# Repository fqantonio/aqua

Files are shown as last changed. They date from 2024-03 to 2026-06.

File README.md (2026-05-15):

# GENERAL VIEW

> Portugal is 97% water [^1]

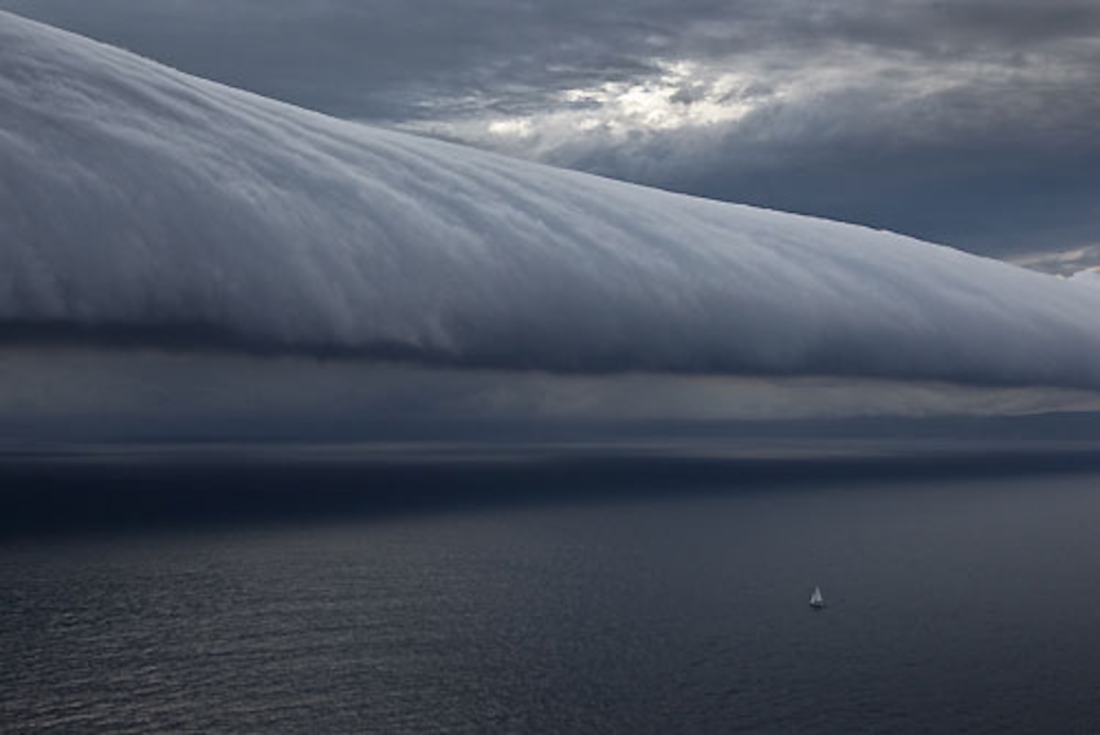
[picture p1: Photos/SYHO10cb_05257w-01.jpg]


*The southerly buster storm front rolling up the New South Wales South Coast, ahead of the first night at sea, after the start of the Rolex Sydney Hobart Yacht Race 2010, Australia. Photo © Carlo Borlenghi / Rolex. www.carloborlenghi.com.* 

## ABOUT AQUA

AQUA is a small autonomous vessel designed for biowater research and aquatic engineering education. This project's core strategy is to consider environmental sustainability from start to finish. All stages, from fabrication to the end of life, should be environmentally friendly.

The team's values are rooted in the **4R's (Reduce, Reuse, Recycle, Recover)** and **circular economy principles**, aiming to meet these standards by at least **70%**. The project also seeks to raise awareness about water and ocean systems, which is especially important since **Portugal's territory is 97% water**.

## MISSION

The goal is to construct an DIY affordable and easily maintainable 1.2-meter catamaran from mostly sustainable materials. This vessel will be designed for a 10 kg payload capacity and at least 2 hours of autonomous operation. 

A crucial part of the design is making it a flexible platform for various research applications, with accessible mounting points for both internal and external sensors.

The goal is to provide the research community with a simple, easy-to-repair, and **open-source water platform system**. The vessel will be constructed using **3D printing** with materials that are biodegradable. 

This approach ensures environmental friendliness from the initial conceptualization to the end of its service life. What should it be used for after that? Its components are designed for reuse.

## TECHNICAL SPECIFICATIONS AND OPERATIONS

The electronics consist of a **Pixhawk Pro** controller integrated with a **u-blox NEO-M8N GNSS module** and a **Flysky i6 8-channel radio transmitter**. Propulsion is provided by two **200W BlueRobotics T200 thrusters** configured in **differential thrust mode**. The system runs on **ArduBoat** firmware and is managed via **Mission Planner**. Currently we use Ardupilot software community Mission Planner 1.3.83 and ArduRover version 4.6.2 on Pixwack.

Lighting includes three normal navigation lights for vessels under 12 m and 6 m (we will read the updated legislation about USV operations): white, port (red), and starboard (green). The vessel features a dedicated structure for video equipment and sensors, and has been successfully tested with a **5kg payload**.

It operates with GPS way points, radio control and its design to be a platform for research, with a battery life to last for 6 to 10 hours depending on the velocidity use: it's design for low speeds, 1 to 2 m/s (4 to 7 km/h)(2 to 4 knots).

In the future, the vessel will operate using manual control with a video display, GPS waypoints, and an autonomous collision avoidance system. It is designed to be **user-friendly**, built with affordable, readily available components, and simple to repair. 

## VESSEL DESIGN & FUNCTION

This **1.2-meter-long catamaran** is intended for use in calm, inland waters during good weather conditions with 50 cm waves. It is autonomous and carries a structure to transport sensors for gathering local physical and chemical data.

## VISION AND IMPACT

We believe this project aligns with a crucial strategy for Portugal: taking care of the sea by learning about it and defending it as a long-term asset. This initiative can serve as a major footprint for the nation's commitment to marine environmental stewardship.
This project is documented as a journal in the file with the name "journal".

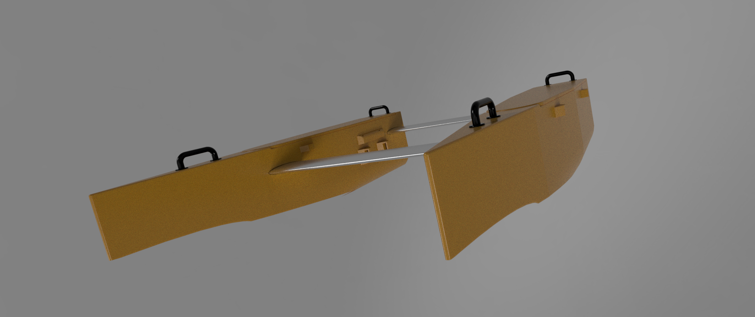
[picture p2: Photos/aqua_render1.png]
First Render of AQUA


# FEATURES

- A Simple Aquatic Robotics Platform for Training, Education, and Research
- Reusable, affordable and biofriendly up to 80%
- Low cost, simple use, acessible and cheap maintance
- 5 kg payload (tested: we plan to test 10 kg)
 
# TEAM
António Gonçalves, Lab Aberto FAB LAB coordinator and teacher, project coordinator and aqua system assembly and control;  

Nuno Gomes, teacher at ESAD - IPLEIRIA and Innovation Makers Labs, Designer Director;  

David Rodrigues, PhD, ESAD - IPLeiria, avoidance systems; 

Henrique Cristo, Physics Engineer student, IPLisboa, sensors structure;

# WE ARE HERE

```geojson
{
  "type": "FeatureCollection",
  "features": [
    {
      "type": "Feature",
      "id": 1,
      "properties": {
        "ID": 0
      },
      "geometry": {
        "type": "Polygon",
        "coordinates": [
          [
              [-9.45,39.5],
              [-9.45,38.7],
              [-9.1,38.7],
              [-9.1,39.5],
              [-9.45,39.5]
          ]
        ]
      }
    }
  ]
}
```

# HISTORY
It all started here, at FAB ACADEMY 2019, held in FCT FAB LAB at Nova University, Caparica Campus, Almada, Lisbon, Portugal [FAB ACADEMY 2019](https://fabacademy.org/2019/labs/fct/students/antonio-gomes/). This was the final [incompleted] project, at the [FCT FAB LAB](https://www.fctfablab.fct.unl.pt/), Filipe Silvestre, as the local instructor and Luís Carvão, as the node instructor, course coordenated by the [FABACADEMY](https://fabacademy.org/), by professor Neil Gershenfeld.

Since then, the Lab Aberto FAB LAB have supported two catamarans made by our intership (Guilherme Cruz) and by the Lab Aberto team, with that they were the winners of 2018 Sunset Hackathon in Ilhavo (Aveiro - Portugal). 

At this moment we gather, informally, a few expertises of different areas to develop a project that need time to set the hulls on the water. We have also another "AQUA" which is a body board with same components to serve as pilot test platform, owned by tha Lab Aberto FAB LAB assotiation. And we are a spinoff of LAB ABERTO FAB LAB, building a first prototyping more close to a small catamaran vessel for inside water bodies training and research.

After being tested, our aim is to share it with MARE in Peniche - Portugal (this is a department of the Polytechnic Institue of Leiria) for further testing in a real framework of researchers and students. 

# PROJECT STATUS

April 2026, GPS grid and RTL tested with an amazing [ESTM](https://www.ipleiria.pt/estm/escola/quem-somos/estm/) student team. Designing V2. Testing, testing and testing.

The work with teachers and students of ESTM was amazing. A big thank you to all of you! During this two days we discuss Computer Vision, 3D printing design and operating AQUA.

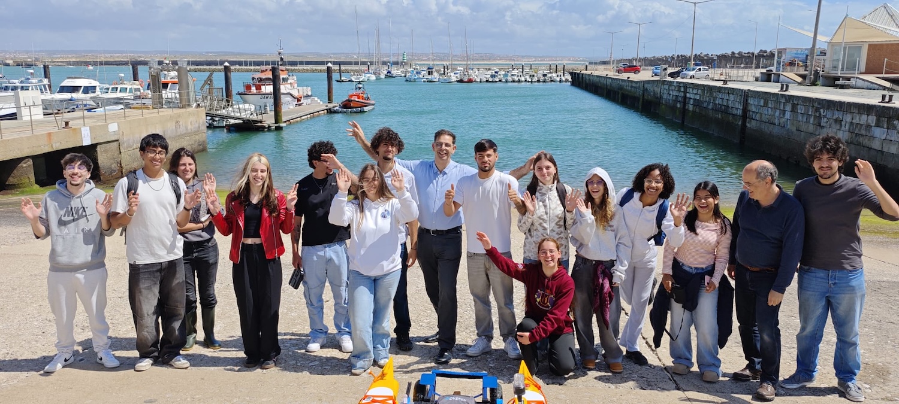
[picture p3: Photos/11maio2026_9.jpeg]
Team work


Credits: Raul Bernardino, ESTM

[https://youtube.com/shorts/ug1nrqGwPGw](https://www.youtube.com/watch?v=cyJqywh_yzk)

# SUPPORT

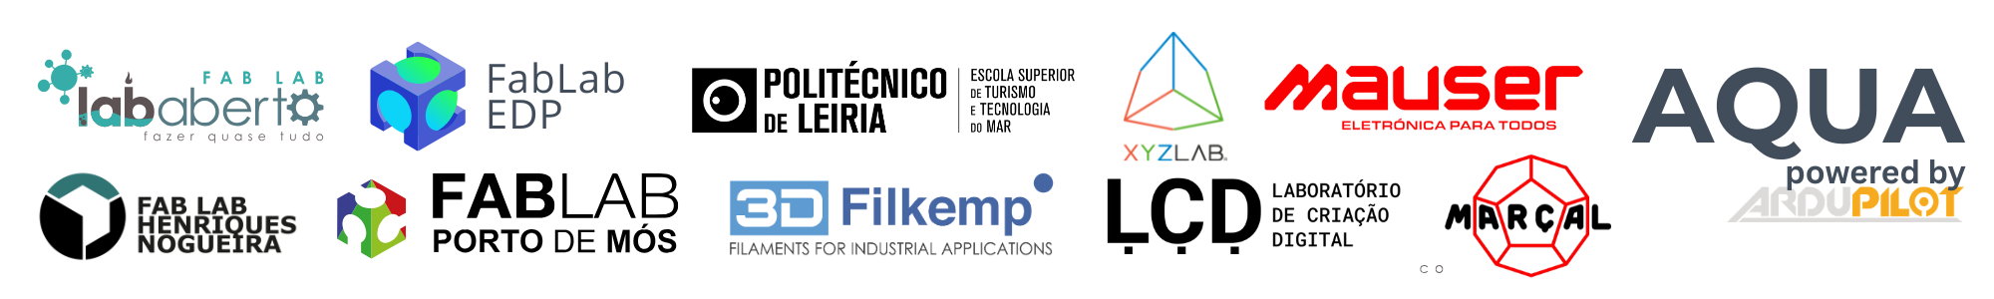
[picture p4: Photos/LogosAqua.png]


 - Associação Lab Aberto FAB LAB, [non-profit association](https://lababerto.pt)
 - António Marçal, advising and workshop space, Marçal Metalworking
 - Marko Mauser, [Mauser](https://mauser.pt/)
 - Paulo Teixeira, 3D printing, [FABLAB EDP/Labelec](https://www.edp.com/pt-pt/inovacao/fablab)
 - Gonçalo Pereira, batteries training and electric circuit adviser, [LCD Porto](https://lcdporto.org/pt/pagina-principal/)
 - Rui Infante, FAB LAB Porto de Mós, CNC milling
 - Tiago Elias, Maker, Mauser, 3D printing
 - Álvaro Brito, MAKER, 3D printing
 - Sebastião Bizarro, Maker, CNC milling
 - Renan Portocarrero, MAKER, 3D printing
 - Alexandre Nunes, Intership, 3D printing and testing
 - FAB LAB HN, CNC milling
 - João Alves, Estagiário da ESAD
 - Nuno Valadas, Filkemp, https://filkemp.com/ 
 - Lagoa do Falcão, Torres Vedras

# CONTACT

aquausv@gmail.com

[^1]: Mapa onde se mostra que 97% de Portugal é mar chega hoje às escolas: https://www.publico.pt/2014/04/02/ciencia/noticia/mapa-que-mostra-que-97-de-portugal-e-mar-chega-as-escolas-1630635, Jornal Público

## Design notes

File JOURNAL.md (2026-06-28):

# 2019

## July ##

### Idea project summary: Sustainable Autonomous Catamaran (USV)

Design and build a **1.2m autonomous catamaran** with the following specifications:

* **Capacity:** Support a **10 kg payload**.
* **Endurance:** Minimum **2-hour** continuous operation.
* **Sustainability:** Constructed with **at least 70% sustainable materials**, utilizing **3D printing** techniques.
* **Modularity:** Designed for easy integration of internal and external sensors.
* **Maintenance:** Focused on **cost-effective** and **simple repairability**.
* **Lifecycle:** Includes a planned strategy for **after-service use** (recycling or repurposing) with a conducted a **Life Cycle Assessment (LCA)** to ensure cost-effective repairability and a circular economy approach for **after-service use**.

---

It will uses modeling and 3D printing with PLA, with the possiblility of exploring new ecofriendly materials: environmentally friendly from the very begining of the conceptualization until the moment that is out of service.

The control, in a early stage, is by radio and GPS way points using Mission Planner of ARDUPILOT software opensource community. If needed could have an avoidance system. ARDUPILOT, is an open-source autopilot software suite where mission Planner is a product. 

The energy system should use Samsung 18650 cells in a two bateries 4S4P setting in paralell (16.8 V). This system can be charged with solar pannels or a 220 V home energy source.

For the spare parts it should have cheap components easily available on the market.

All started here, at FAB ACADEMY 2019, held in FCT FAB LAB at Nova University: https://fabacademy.org/2019/labs/fct/students/antonio-gomes/projects/final-project/

After the pilot-project there will be a **Life Cycle Assessment (LCA)** study.

# 2023

## July ##

Restart after the pandemic. New CAD design. Finding partners.

## September ##
Printed parts at MAUSER 3D printing services:[MAUSER](https://mauser.pt/catalog/)

### Security ###

Using gloves and special masks.

# 2024 #
## Jannuary ##
Glueing the parts at the António Marçal workshop.
We are using the bodyboard as a testing for all of the processes.

| Workshop overview process! |  |  
| ------------- | ------------- | 
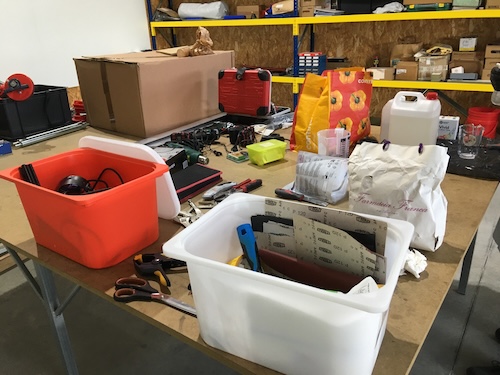
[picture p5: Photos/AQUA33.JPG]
|  |  | 
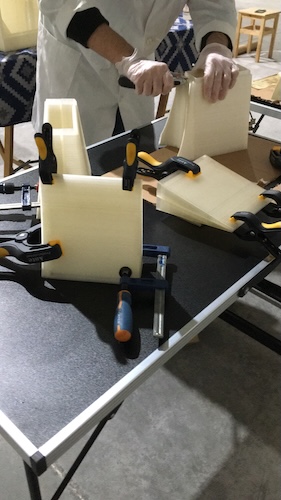
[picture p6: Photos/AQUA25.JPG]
|  |  |
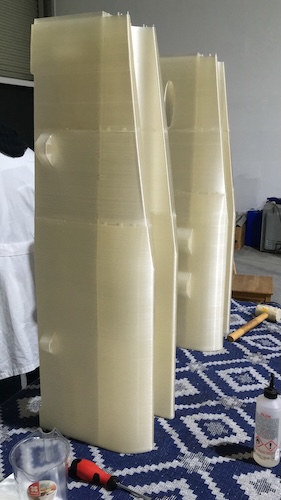
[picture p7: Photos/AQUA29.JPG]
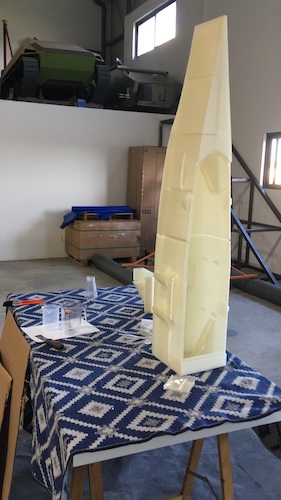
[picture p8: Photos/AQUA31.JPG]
|  |  |

## February ##
Resin the hulls. Because of the weather its was a very slow process. 
We never reach the minimum temperature of 21 degrees and 60% of humidity.

| **Resin the hulls** |  |  
| ------------- | ------------- | 
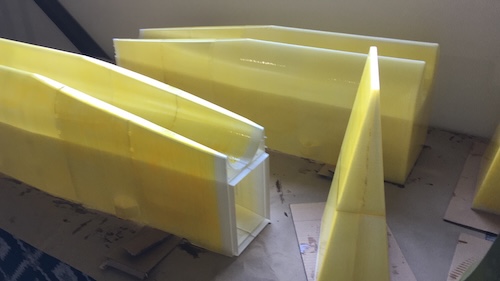
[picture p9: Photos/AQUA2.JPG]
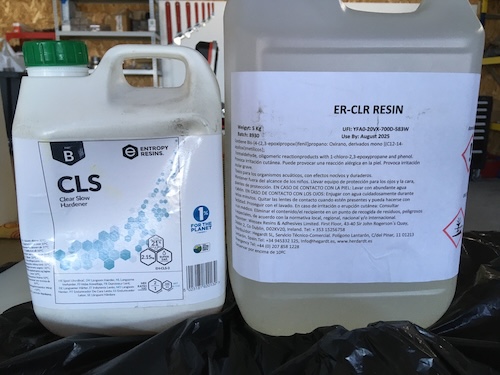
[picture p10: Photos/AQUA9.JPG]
|  |  |

As you can see, there is a chemical reaction between the resin and the paint. The good news is that, if you repaint, it will vanishes! great!!!

| **Resin the hulls** |  |  
| ---------------- | ---------------- | 
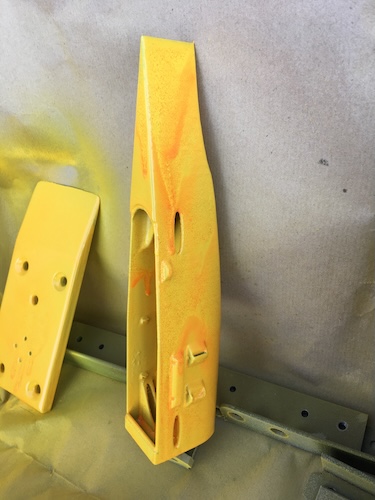
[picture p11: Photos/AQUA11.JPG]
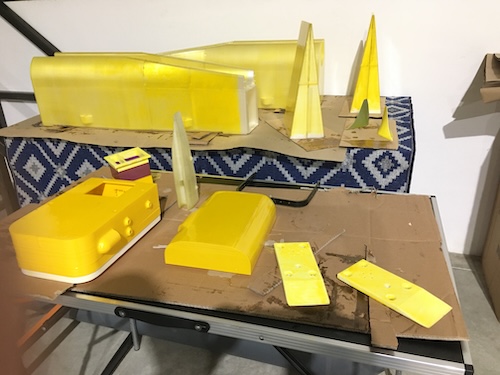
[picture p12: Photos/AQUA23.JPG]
|  |  |
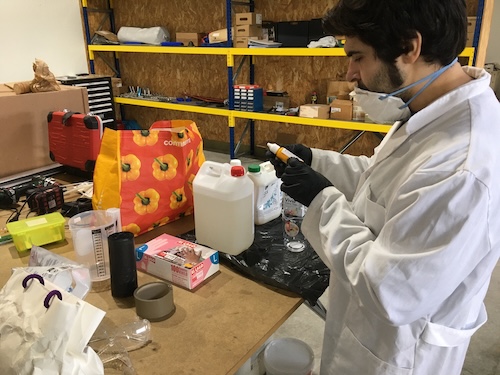
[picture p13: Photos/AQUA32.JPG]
|  |   |

| **What amount of garbadge!?!?** |  |  
| ---------------- | ---------------- |
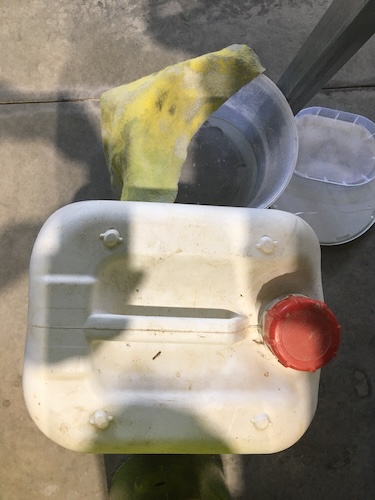
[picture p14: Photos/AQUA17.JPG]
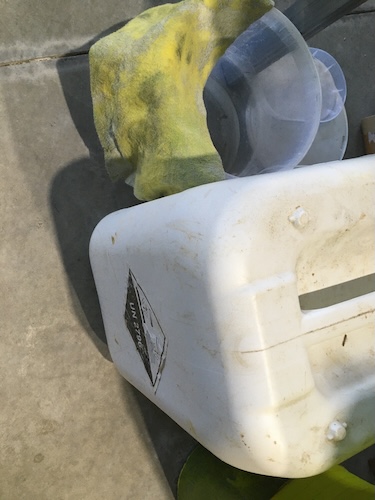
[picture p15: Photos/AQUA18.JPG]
|    |    |
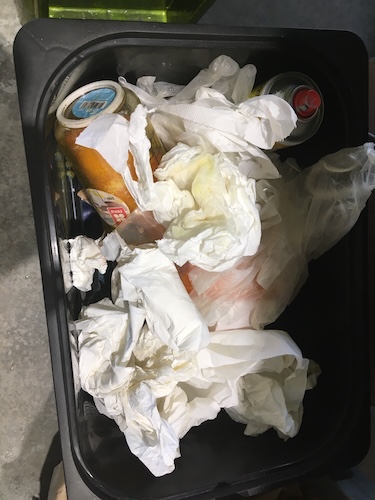
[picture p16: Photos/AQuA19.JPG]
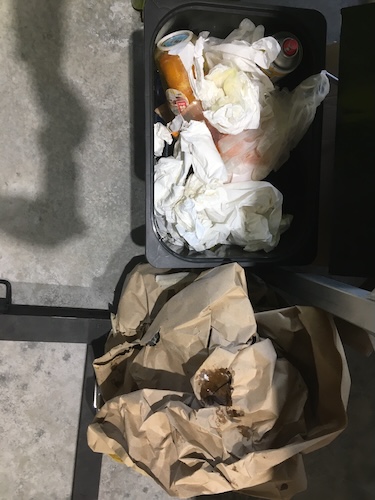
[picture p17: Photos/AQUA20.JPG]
|    |    |

Primary painting. All the errors appear!

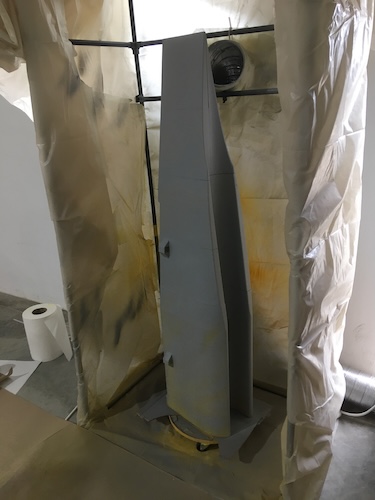
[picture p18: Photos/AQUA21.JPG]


## March ##

Fill the holes and repaint after sanding, sanding and sanding. Repaint again. This process is not going well because it continues to react showing spots of orange (see pictures). We think to change the process in order to have more 3D printed only and putting the UV paint only. It avoids a lot of work and mess.

## April ##

| In April we finnaly concluded the painting. |  |  
| ------------- | ------------- |
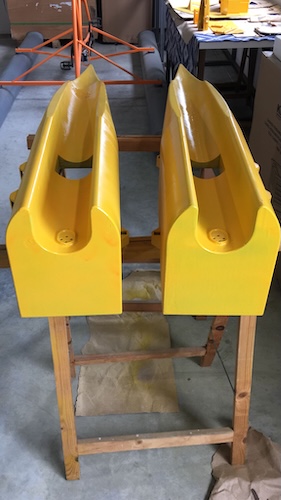
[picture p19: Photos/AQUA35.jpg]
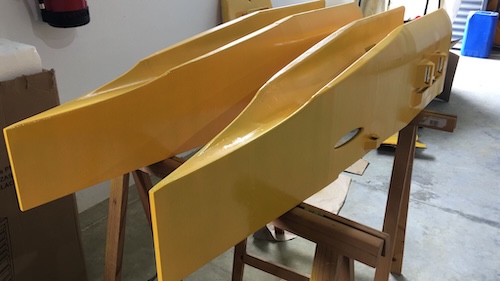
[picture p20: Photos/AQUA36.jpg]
|  |  |

We did the UV paint with this brand.

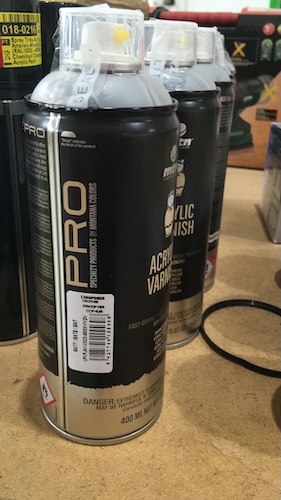
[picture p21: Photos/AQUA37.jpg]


The process is not environmentally friendly as we suspected: so, we plan to produce this catamara in a different way by taking the 3D printing strategy further, meaning that, we do not wanted to add to much to the 3D printing process, just the UV painting, and we want to assume the 3D printing "anommalous" desing by not be embarassed because of this consequent strange design. We will not 

## May ##

Spaghetti time! Designing the wiring and accomodating the hardware to control the AQUA.

| Control  |  |  |
| ------------- | ------------- | ------------- |
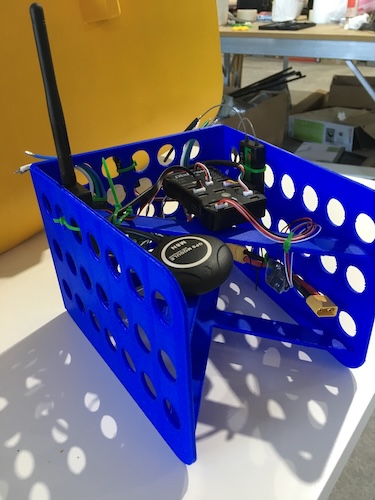
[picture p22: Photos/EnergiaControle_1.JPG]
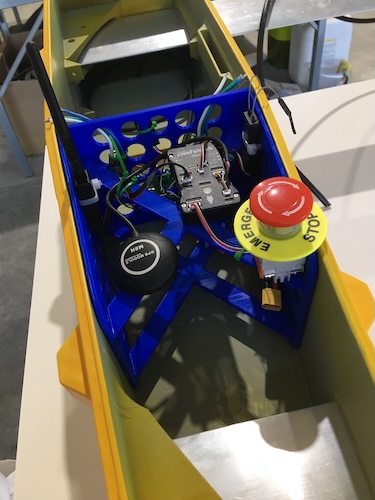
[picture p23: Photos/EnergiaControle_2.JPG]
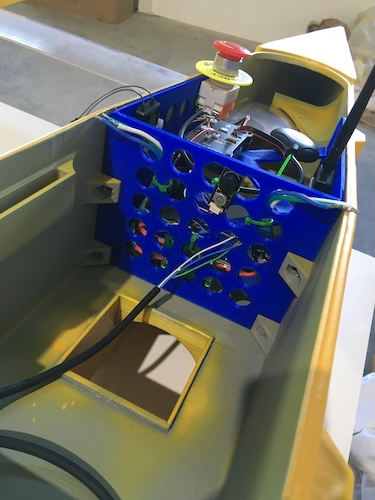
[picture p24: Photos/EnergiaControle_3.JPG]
|  |  |  |

We are also looking the way to adjust, with flexible material, the front and rear bars that go inside the boat. They are connected by two screws in each side.

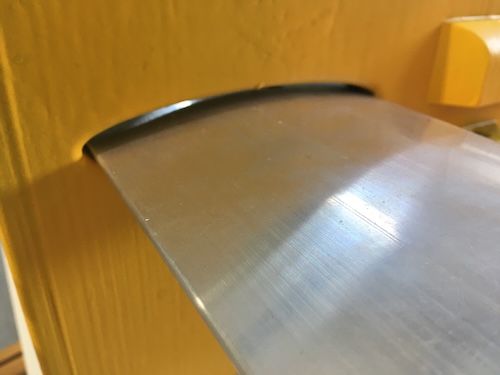
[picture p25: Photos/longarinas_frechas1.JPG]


Future: looking forward to test it in a pool. 

## July ##
Cleaning was a task at this point and measuring the type of garbage and the weight in percentage of the catamaran is a reference to take the sustainability into account. The complete weigth of the catamaran is 20,5 Kg with an error of 0,2 Kg. So the waste produce in the fabrication of the catamaran was 22,1 Kg this time, 107,8 % of the mass of the catamara. 

Since we don't know how to process this catamara in is end of life, we coclude that, at that time, there will be 42,6 kg of waste, which include eletronic parts and plastic less environmentaly friendly. So, in the end of his life there will 207,3% of waste, compared to the mass of the catamaran.

| Type  | Weigth (kg) | % |
| ------------- | ------------- | ------------- |
| Paper  | 1,2 | 6 |
| Cardboard | 5,6 | 2,7 |
| Plastic  | 5,8 | 2,8 |
| Painting cans | 1,8 (18 cans) | 0,1 |
| Metal | 3,4 | 0,2 |
| undifferentiated waste | 4,3 | 0,2 |

| In July we stop here...  |  | |
| ------------- | ------------- | ------------- |
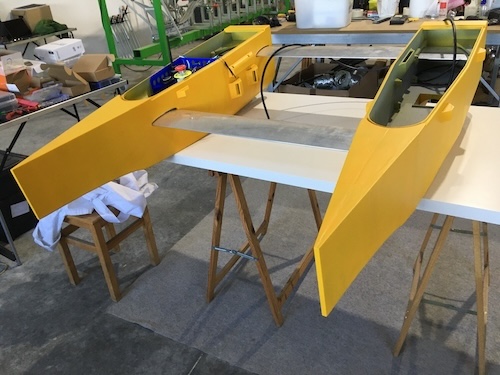
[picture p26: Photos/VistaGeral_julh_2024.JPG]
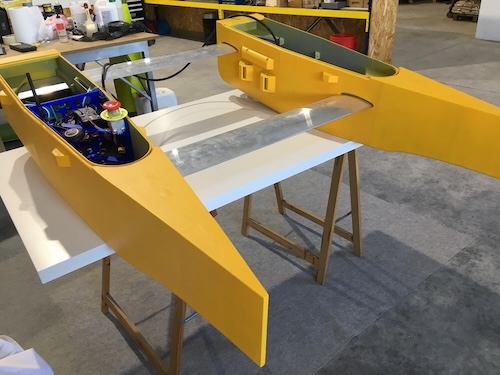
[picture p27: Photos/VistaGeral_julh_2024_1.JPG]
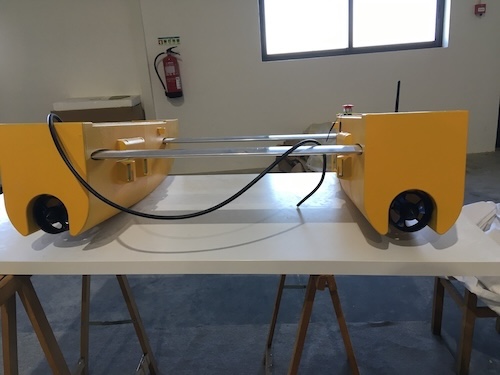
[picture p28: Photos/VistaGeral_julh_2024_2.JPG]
|  |  |   |

## September and October##

This month is devoted to plannning and assembled the top, cameras, antennas and water test.

## October ##

This month was devoted to plannning and assembling and redesign the power circuit.

## November and December##

Test the microcontroller circuit and the power circuit as well. Radio transmitter settings. Ground and Water tests. Spagheti time! Designing and accommodating all the wiring and hardware components to controle the AQUA. We will use ARDUPILOT in is boat (rover) version: tested and working properly!



## January 2025
Remodeling 3D and printing electronic box. Printing and modeling the battery holder. Built 4S4P batery with the help of LCD Porto Maker Space, by crimping.

| Energy! | | 
| ------------- | ------------- | 
|  |  |
|  |  |



## February
Buoyancy testing.

| Is it a submarine or not? | | |
| ------------- | ------------- | ------------- |
|  |  |  |

We found a structural break in the hull. Perhaps because of a falling situation when removing from the car. Preparing to fix it.



We are going to try to fix it. 

We reprint the access hatch in the top of both hulls with less holes then before, since we decided to have only one openning for the telemetry antenna. This aquatic plataform will serve as a base to have anything that the school need. We reprint the eletronic box and made the battery 4S4P.

## March

Structural break fixed. After sanding and cleaning with a dremel, and prepared the epoxi glue the results:



Thinking about the unbalance hull. That's a big issue that didn't appear so important but with the real hull it appears very disturbing. Two solutions, taking in account that this is a prototype: 

1. modeling a boid to attach to the bow in order to balance it;
2. glue a foam under the bow.



# Tasks
- [x] Structural break;
- [x] Assemble the last cleat;
- [x] Glue the foam to the bow;
- [x] Paint with yellow and varnish;
- [x] Attach security light
- [x] Testing...

## May

| painting | | 
| ------------- | ------------- |
|  |  |

The top covers were left unvarnished to directly observe the behavior of the PLA material and compare it to the varnished sections. Foam was adhered to the underside of the hulls to enhance the catamaran's stability. Elastic structures were integrated to securely fasten the covers. Finally, the last coats of paint were applied, and the top hull covers were tightened to improve water tightness. The paint didn't work weel in the foam.

| painting | | 
| ------------- | ------------- |
|  |  |

- [X] Remodeling the top hull covers in order to be more water tight;
- [X] Fix the hatchs with holding belts;
- [X] Make the second 4S4P batery;
- [x] Print the batery holder;
- [x] Security safety buoy;
- [x] Seal the motor holes in the hull;

## June

We have made a heavy testing of the boat. Even the transportation was a testing point. The boat is to wide for the van. yes!!! Wrong turn!!!We need to cut the floats stringers by 7 cm. 



The heat was another testing point. 



The top covers were replaced because the rubber fixers where not appropiate for the heat during the transportation incide the van. The new top covers where made with EPS machineed at the Porto de Mós FAB LAB.

| CNC FAB LAB Porto de Mós | | 
| ------------- | ------------- |
|  |  |

We also print parts to insure that the water doesn't get inside the hulls. We also modeled fixers for the top float covers that use straps .



This is crucial. We need to glue the front floaters or the boat will not be horizontal in the water (see February pictures). During the transportation they got out. Another wrong turn!

| Wrong turn | | 
| ------------- | ------------- |
|  |  |



## July

- [x] Second batery on the 3D printed cover
- [x] Screw the motors better
- [x] Check the electrical cables fixation
- [x] Presence light (not only for the night but to test the transmiter connectivity to the system)
- [x] Testing the boat by radio controler and GPS waypoints;
- [x] Testing testing testing...
- [x] Transportation in the field
- [x] Minimal tools
- [x] Using procedure

Tomorrow I'm going to assemble the engine. It was removed when I moved it on the table. Issues around the use of the boat.



Boat ready to test. We machine the parts on the FAB LAB CNC machine of Porto de Mós FAB LAB. Fix them with flat ropes.



## August

Tests on 10 August. Add a handcart to move it easily.





It goes ok as you can see in the video. The bow is a little bit down but we will add more flutuability in the next iteraction. Everything was fine... When I opened it, it has water inside!!! Brr....

In the next day I weard water moving also inside. The boat is taking on water, I don't know where from. I should none that because hobbiecat does that...

Water testing.



### UPPS!
Water is coming in through the four screw holes and the both electrical wires that powers the engine. But it doesn't go directly into the boat, it enters the hull and then comes out through interior grooves in the bow... that are result of the way the boat was built... I'll insulate it as best I can... and hope for the best. I use silicone in the wire hole and the screws.



Notice that the starboard paint peeled off.



Using the air compressed most of the paint went off.

| air compressed| | |
| ------------- | ------------- | ------------- |
|  |  |  |

| peeled off | | |
| ------------- | ------------- | ------------- |
|  |  |  |
|  |  |  |
|  |  |  |
|  |  |  |
|  |  |  |
|  |  |  |

Repairing again using primary and epoxy paint. Better sunding for adherence.

| Repairing | | |
| ------------- | ------------- | ------------- |
|  |  |  |
|  |  |  |
|  |  |  |

Thruster reparation.



Addint the feature of measuring current and voltage.



Apply silicone... dry for 6 hours and put it on water again.



Took water inside again but less... but it worked... buzzer ringing again.
Interior water also. F...

Today, Sunday, it's drying! I put it back also. Lift it in several positions for the ware to came out from the grooves: it was upside down because the water comes out inside, at the stern, and then drains inside, but at the top of the hull.
when tilted, you can no longer hear the sound of water inside.



Possible entries points. Need procedures to handle the boat. I will try to test the way points. In spite of not having internet on the locals we can use fetching with MP.

| Water | | 
| ------------- | ------------- |
|  |  |

### CONCLUSION

Water is coming in through the four screw holes and the both electrical wires that powers the engine. But it doesn't go directly into the boat, it enters the hull and then comes out through interior grooves in the bow... that are result of the way the boat was built... I'll insulate it as best I can... and hope for the best. I use silicone in the wire hole and the screws.

No data collected yet... just see what's going on: audible warnings that needed to be understanded, seems to have same battery heating (we should have an internal temperature sensor). Strange sound... try to understand what it means... it's not from the pixwack because we don't have the buzzer (well, we don't have it now but we had it, it broke)... but the button to start the engines before arming in the MP software... it has... investigate what it means. It working alright. We plan to repaint the hulls in October. So, we will came back to it in October, now, vacations!



Video: https://www.youtube.com/watch?v=jL261LpirRE

## September
Repaint everything. Hard work that need to be done! Paint, holes repair and primary

| Paint | | 
| ------------- | ------------- |
|  |  |



All set disassembled.



Minimal tools to disassembled.



Destails, starboard and port board.

| Details, details | | |
| ------------- | ------------- | ------------- |
|  |  |  |
|  |  |  |
|  |  ||

Eletrical part.



### WARNING!!!
Reparing the boat more carefully confront us with the epoxy problem, that came out to be a problem:
1. Waterproof epoxy: we didn't use it;
2. We should had sanded the PLA to create roughness;
3. The preparations painting stages and the wating times are crucial to have a good result: so, reading the technical documents its crucial

Always learning in the hard way.

Next: Repairing. Painting. We also had to change the T200 thrusthers because, whenever we put the floats in the horizontal we didn't notice they they slihtly touch the ground and the structure broke.



## Blue fest

Dia 1, 
3:50, 16:50, 40:00, Applications (Aplicações)
https://www.youtube.com/watch?v=jmRiKE0HMcY

Dia 2, 
57:00, Blue tech Academy school (Escola)
https://www.youtube.com/watch?v=pink51yKz9M

Extend you radio range WIFI communications: https://www.youtube.com/watch?v=TAoYp5voIo8

Dia 3, 
4:35, Training and edu (Escola e formação), 
28:00, Seaweed (Algas), 
40:00, Corals, 
52:00, Photogrametry with a sonar (fotogrametria com um sonar)
https://www.youtube.com/watch?v=Y_22u3cKbTw

## October

- [x] Valves: buy
- [x] Engine covers, buy
- [x] more flutuability to the bow: improve with a bolt...
- [x] BUY the flag
- [x] PVC for the holes of the motor atachment
- [x] Buy lights: white, red, green!?
- [x] Procedures
- [x] repair and paint the hulls (see procedure bellow)
- [x] Charging procedure: improve circuit and carefully with both bateries in mind;
- [x] print and paint 3d float part;
- [x] Reassemble the T200   
- [x] GPS problem: no led light blinking...
- [x] strange warning PIXWACK beeps!? They were from the safety switch (https://ardupilot.org/rover/docs/common-sounds-pixhawkpx4.html#common-sounds-pixhawkpx4)
- [x] test the voltage accuracy;

We followed this **paint procedure**:

1. 3D printing the bow floats;
2. Sand the hulls to remove the paint as much as possible (120 to 220);
3. Prepare the holes for the bow floats, thruster cables, valves and the three lights (red, green and white);
4. Close the holes (prepare the repair compound using two spatulas: just a drop of hardener is enough);
5. Wait 24 hours;
6. Sand the parts where we applied the repair compound;
7. Clean with a sponge;
8. Apply epoxi primer with the paint roller and brush: after preparing we have two hours to apply it;
9. Wait 1 day and paint: if you can't, wait 5 days for the paint to become glazed, sand again with 220-grit sandpaper and paint (the sanding is for the paint adhesion);
10. Certify that there are no "holidays": repaint if needed with the primer mix with thinner (not to much, just to loar a little bit the viscosity;
11. Apply yellow enamel paint (polyurethane plus acrylate) with the roller and the brush:
    (a) stir well before mixing;
    (b) make half and then the rest if needed: after two hours the rest is not reusable: clean the brush with thinner and throw away the rolls;
12. Wait two days;
13. Repaint if needed using a little bit of thinner;
14. Mount the structure, flag, lights, batteries, eletronics and eletrical parts;
15. Test, test, test and test!

| Repair | | 
| ------------- | ------------- |
|  |  |
|||

After the repair, testing. Everything is working.




But, it sudendly stoped because the electric terminals that I use in the thrusters wire didn't handle the high current. The "strange warning PIXWACK beeps!?" where not exactly from pixhwack but from the safety switch buzzer saying thta the batery was low.
After this repairing the boat was tested and more water inside... grrr.... everywhere, from the hulls (more on the starboard) and small floats on the bow.

| Water inside | | 
| ------------- | ------------- |
| |  |
|||
|  |  |

| Repair | | 
| ------------- | ------------- |
|  |  |
|  |  |
|  |  |
|  |  |

Try to dry everything;



remaking holes, because the wire of the notors where to curved; holes for the Thru Hull at stern;

| Repair | | 
| ------------- | ------------- |
| |  |
| |  |

Lights where a nightmare! After trying to understand all the documenting about ardurover firmware outdated; finnaly though that it was tight, but no... I even get a multimeter and an arduino uno to see what happen to the pins when I was pushing the radio button to turn on the lights... they seemeddead. Why are they all dead? Seeking to find same parameter in the thousand of parameters that keep the pin LOW. Well... it was just a button: push the safety button because, if not, pins are no enabled!!! Grrr...

We have lights! White, red and green.

AQUA is assembled again, with valves and lights: ready to be tested.
The test when good for about 30 minuts but it starts to be get water inside again. At the same time one of the switchs broke, I don't know if because of heat (high currrent) or another reason. The main switch is bronken. Changed! Everything seems ok now. All the lateral conections between the aluminium bars, the stringers, and the floats where filled with silicone. After drying we will test again.

| Sealing | | |
| ------------- | ------------- |------------- |
| |  ||
| |  ||
| |  ||

Restart again... Everything on the boat must be very well sealed. Today we tested again and it works very weel; there is, still, some water in, but it's a small quantity, and we will reseal again.

Problems: battery warning are not consistent with the measuring; warning of the giroscope calibration are confusing because the calibration was done and in the past we never get it. Problems with the normal driving mode; a little bit of water: resealing!



Testing the layer height and the number of walls.

| Sealing | | |
| ------------- | ------------- |------------- |
| |  |  |

Results: no spilled water 

Conclusions: We think that 3 walls are enought

 

 About the garbage, in total 12,4 Kg this time, there are some that its clear where to dispose, other its a mess. Adding the waste in

| garbage | | 
| ------------- | ------------- |
| Plastic | 3,4 Kg |
| Paper | 6,5 Kg |
| Paints | 2,5 Kg |
| Bateries | 16 AAA bateries |

Until today, the waste produced was 34,5 Kg (168% of the mass of the catamaran); if we had the material in the end of life of th vessel, it will be 55 Kg, 268 %.

## Faires and conferences

1. STE 2026, Porto, 1-2 October
https://engeduconferences.com/STE2026/
2. Put the project online here: Nautica expo
https://www.nauticexpo.com/pt/
3. Madrid, Junho 3-5, startups, South Summit
https://www.southsummit.io/
4. Lisbon Web Summit 2026
   https://websummit.com/

Professionals faires (to be discussed):

4. Oceanology international, Londres, 10-12 março 2026
5. Isobay, 16-18 junho, Basc Country
6. Conference, https://www.it.pt/Events/Event/4345
7. https://www.infratech.de/en

## November/December 2025

This november we had a benificial meeting with [ESTM](https://www.ipleiria.pt/estm/) Politenic University school belong to [IPLeiria](https://www.ipleiria.pt/) where the sea and water areas are important for their biology research and training teams.

It was decided that we will start a program from March 2026 to July 2026 to test, use as a pedagogical tool and as a platform fro plancton research.
So, our major task now is to prepare everything in order for ESTM has the best experience with our USV platform. And we are also keen to know the reception in March and the outcames in July.

For now this are the tasks until **March 2026**: prepare, prepare and prepare, and test, test and test!

- [x] Buy the radio receptor with 10 CH
- [x] MP parameters: see discussion on ArduPilot Discourse about AHRS warning;
- [x] Presentations and faires
- [x] Publish the testing walls and layer height results and conclusions;
- [x] Milling the covers
- [x] reseal;
- [x] giroscope calibration warnings: first time;
- [x] Battery safety switch warning;
- [x] Nicla Vision WIFI: print and assemble
- [x] Contact enteties for a broad protocol
- [x] Review material waste weight: Publish the garbage update;
- [x] driving mode decision;
- [x] Get test sites maps with MP fetching;
- [x] Write the procedures manual to handle the boat carefully: before, during and after;
- [x] email entities for logos
- [x] VRA and VRB Flysky Radio ready to use

In this month, we prepared the covers to be more user friendly. Ready for the third round of tests!
MANUAL, AUTO, ACRO!? or LOITER!? (https://ardupilot.org/rover/docs/loiter-mode.html); other: simple (https://ardupilot.org/rover/docs/simple-mode.html), GUIDED, PosHOLD; RTL; SMART RTL; ACRO; HOLD; STABILIZE: choose! https://ardupilot.org/rover/docs/boat-configuration.html; https://ardupilot.org/rover/docs/rover-control-modes.html
VRA and VRB Flysky Radio ready to use by choosing menu OPTIONS in FLYSKY i6X, AUX. Channels, channel 9, source VRA and channel 10, source VRB;
Use VRC e VRD as 6 position navigation mode: for a nice explanation follow this video: https://www.youtube.com/watch?v=0BVSjSCz8f4&t=141s

## Problems

We choose the normal, auto, loiter, guided, ACRO and SRTL.
We had problems with the battery safety warnings saying "unhealthy batery": solution was within the power module selection for voltage and battery capacity;
We also had problems with unhealthy AHRS: we did a acceleration calibration only with the pixwack box and not with the entire AQUA;
Problems with the compass: alighn N-S and mag recal and reboot.
At this moment no problems with water inside.
Problems with the telemetry antenas. It fall down around 15 meters... the issue a missing pin...



This raised the issue of the **radio frequency** rules in Portugal: we can use the 433 MHz but with a maximum power of 1 W: https://www.anacom.pt/streaming/anexo2.pdf?contentId=797080&field=ATTACHED_FILE

The logistics is an issue to tackle in february, because getting wet when putting the vessel in the water is a problem and transporting it, another one.





Defining the minimum number of parts to control AQUA when in operation, including tools that could be available or not to the regular user.



This are photos about this AQUA USV stage:











Video:
https://youtube.com/shorts/ug1nrqGwPGw

Logos of the partners:













AQUA run arount 1h:15min and use 80% of the batery and it showed the safety batery sound warning. this is because there a diuference of 1 V between what the power module is measuring and what the voltmeter register. Calibration needed.

## Jannuary 2026

- [x] Calibrating the voltage and current measure in MP software parameters;
- [x] buy a USBC longer cable;
- [x] Test autonomy;

Consumes 5% of energy in 40 minutes at a speed around 1 m/s (4 km/h) speed. So, up to 80% will have an autonomy of 160 minutes... 2.5 hours. Up to 60%, the limit, 5 hours.
Radio working fine. GPS came late. During one hour didn't connect. In the end of the test it fix with 5/6 satelites. In the second day the same. Never fix and it doesn't show any satelite. In the afternoon I unplug and plug again the GPS and it starts wotking wit 6 satelites fixed. Is it the connector? Will we need a second GPS? With this problem we cannot rub by waypoints. Between measured tension there is a 1 V diference. Need to check again.
Small entrance of water on port hull: bujons need to be better fixed.



Video: https://youtu.be/fWGKFttk83Q

I made this float based on the previous one to see what weight we could achieve. It was reduced to 5 kg, 5 days of printing in four parts, without infill with 6 walls, printed on QIDI, at 200 m/s. This means we can have an AQUA weighing 13 kg instead of the current 21 kg... we estimate that the payload at this moment is a little over 5 Kg, but if we can save 8 kg in the hulls we can gain a payload about 10 Kg.

[STL file](https://github.com/fqantonio/aqua/blob/main/3D/estibordo_V9.stl)

We are going in two problems, Nicla Vision Assembling and GPS powering. About Nicla Vision the issue is how to power up and fix: this pictures shows the status solution:



The other issue its about GPS mentioned above. For now we have this four ways to know if the GPS is working and we have confirmed that is working:

1. Check the HUD (Heads-Up Display) on the Flight Data screen: "No GPS" Message: the Pixhawk cannot find the module. "No Fix" Message: If it says "No Fix," it hasn't found enough satellites yet.

2. View Live Satellite Data
Under the map on the Flight Data screen, look for the "gpshdop" and "sats" values: "sats" shows 0 but the status is not "No GPS," the module is powered and working, just waiting for a signal. Completely blank or "0" while the HUD says "No GPS," the module likely has no power. 

3. Use the Messages Tab 
At the bottom of the Flight Data screen, click the Messages tab: Look for a message saying "GPS 1: detected as u-blox at [baud rate]" shortly after you connect or reboot the Pixhawk. If you see "GPS 1: fail to initialize" or no GPS message at all, it indicates a power or wiring issue. 

4. Hardware Verification (MAVSerial Pass-through)
In Mission Planner, press Ctrl+F and select "MAVSerial Pass". If u-center can see the module, it is powered and functional. 

The next issue is: what is delaying the GPS so long? Gemini AI say this: M8N Pixhawk GPS modules take hours to fix satellites
due to a lack of a valid almanac/ ephemeris (satellite data), often from being powered off too long, significant travel (>100 miles), or poor signal/interference, leading to a slow cold start, with potential issues being battery drain on the Real-Time Clock (RTC) or internal interference from nearby drone electronics (like VTXes or cameras) hindering satellite reception. A good M8N should get a fix in minutes, but hours indicates a serious problem like a faulty antenna, damaged LNA/filter, or massive RF interference. We will stick to RF interference for now and see what happen, because we have the radio antena to close to the GPS. And now I remember that the GPS fix happen when the radio was off: it happen on the Figueira da Foz Port. So, testing that and changing the antennas position. Lets see.

Novalty is to have Henrique on board, hope he have time to join the project.

Nicla Vision is ready! Video: https://youtube.com/shorts/aYXpTuRiET0?feature=share
- [x] pictures here and videos...
- [x] STL here
- [x] Nicla Vision ready

# March
Finnaly we have good weather in our region but the environment were pretty damage with Katrin storm. So the project is delayed by at least 1,5 month, we have to reschedule it. New design hulls is under discussion and it will be printed by Rui (FAB LAB Guarda).

The first meeting with the school will happen on March 11, and we will coordinate with the teachers the three sessions for the students.

GPS seems not to be a problem since we get it outside of the hull. We had a problem with actions window in Mission Planner (MP): with the portuguese language doesn't show all the buttons action, namely, arm (force) and disarm.



Nicla vision is under testing. it seems that is innapropriate for the job.

Battery parameters where changed (see the table in the battery session), from voltage limits, to capacity, cruise velocity and fail safe limits.

About the Gopro camera: wifi, FPV or local recording? We have a plan B for now, using gopro similar and record on a sdcard; the other systm as arrived and, ASAP, we will try to put it on work;

We had the meeting in ESTM and we schedule to working days: April 27st and 4th of May.

- [X] Test the antennas reposition and EM environment inside AQUA using another GPS connected to the computer
- [x] Prepare second ESTM meeting: send plan and set specific goals;
- [x] Battery parameters: see link https://gemini.google.com/share/926e40b1ec7d
- [x] Cruise velocity
- [x] Gopro camera: wifi, FPV or local recording?
- [x] Switches "flight" mode PWM parameters selection
- [x] Outside sensors structure;
- [x] Nicla Vision state
- [x] include calcs for the 4S4P battery file;
- [x] Install Nicla Vision
- [x] Nicla vision battery and magnetic switch

Aqua outdoors Tests
- [x] Test RTL: see this link; https://gemini.google.com/share/926e40b1ec7d
- [x] Test AUTO mode Control and GPS point test, including grid: [Mission Planner (MP)](https://ardupilot.org/planner/); https://www.youtube.com/watch?v=rui2Trps2yc 
- [x] Test Grid auto mode;
- [x] AQUA new design: discuss teh details

# April

- [x] AQUA activity log sheet registering;
- [x] Review procedure;
- [x] Team needed and roleplay: what roles? List of specific tasks; what the goals and what to measure and verify on AQUA operating conditions;
- [x] Prepare 27 APRIL 2026 training: talk to Henrique and David
- [x] revisit minimum tools and tool box
- [x] Revisit the procedures manual to handle the boat carefully: before, during and after;
- [x] Review documentation: STL files, manual, procedures, safety and maintenance;
- [x] Set specific goals for the student training;
- [x] Deliver for training and testing (ESTM IPLeiria);
- [x] ESTM goals: usefull? Usability? Easy to use? Advantages and drawbacks? Improvements? Team work? Learning, competence? Autonomy? Social Interaction? LCA?Collect videos for AI models?
- [x] Problems with the GPS accuracy: try to use in CAN mode wiring: https://www.youtube.com/watch?v=L6gyeE3Q22A

All tested, except, logs data and video captures. 

Problems found:
1. The drain plugs aren't sealing properly: the port side float is still taking water inside.



3. The laptop battery stops responding to Mission Planner (MP) requests once it drops to 60% battery capacity.
4. The sensor structure is wobbling: we are currently assembling an alternative structure with aluminum fittings as a "Plan B." Henrique will later design a 3D-printed solution to minimize oscillations.
5. Nicla vision Battery doesn't charge and it's not robust to be used for intensive computacional vision;

Decisions:
1. abandon Nicla Vision
2. Plane B for the sensors structure
3. Seal the bujons on the port side
4. Buy another battery for the computer

April 27, first operation with students from ESTM school.







# May

- [ ] data record

The work with teachers and students of ESTM was amazing. A big thank you to all of you! During this two days we discuss Computacional Visio, 3D printing design and operating AQUA. They have the AQUA and a 3D printer to tackle two objectivs: get video data and design the sensor struture to secure the sensors box and severaldiferents sensors and capture net for the plancton and plastics data. 











Credits: Sónia Cotrim, ESTM

We have started the discussion of the design of V2 version with Nuno and Henrique. Rui, from FAB LAB Guarda is also in the team to produce the hull in his linear 3D printer.

The next step is to make the co-creation moment with the ESTM students teachers and the AQUA team and partners, next June.

At this stage, we assess the projet, comparing with the goals of design and build a 1.2 m autonomous catamaran Sustainable Autonomous Catamaran (USV), with **80 %** completed. The table bellow show each detail goal.
 
| Goal | State | % | Comments | 
| ------------- | ------------- |------------- |------------- |
| Capacity: Support a 10 kg payload.  | we´ve tested 5 kg | 50 % | |
|  Endurance: Minimum 2-hour continuous operation. | It has 6 to 10 hours of autonomy with max velocity 3 m/s | 300 % | |
| Sustainability: Constructed with at least 70% sustainable materials, utilizing 3D printing techniques. | In this prototype we didn't reach this | 0% | |
| Modularity: Designed for easy integration of internal and external sensors. | Almost there | 50 %| |
| Maintenance: Focused on cost-effective and simple repairability. | Complete | 100% | |
| Lifecycle: Includes a planned strategy for after-service use (recycling or repurposing) with a conducted a Life Cycle Assessment (LCA) to ensure cost-effective repairability and a circular economy approach for after-service use. | not yet defined | 0% | |

| date |	Velocity (m/s) |	Voltage (V) |	Current (A) | Batery % | Observations |
|---|---|---|---|---|---|
|| 	| | |  ||
|  | 	| |  |  ||

| Date| Batery % | Capacity (Start Charging) | Capacity 2 (End Charging) | Operation (h) | Observations |
|---|---|---|---|---|---|
| |  | 	|  	| |  |
||  | 	| |  |  |
||  | 	| |  |  |

# June

This test was a huge frustration!
We have a temperature problem inside the hulls.
It all started well, but when we are in the final process of arming the AQUA via software, there is an indication of only 12V and constantly dropping—even the computer was struggling.
Until everything lost voltage... it never worked again.
It's 4 PM and the temperature is around 40ºC.
The next day, at the Lab Center, everything started working normally, except for one of the batteries which has a faulty cell.
I haven't disassembled it yet, now only after the 2026 bootcamp.
At that time, I will also add some vents and a fan to circulate the air inside the AQUA.
I had already suspected it, because it feels stuffy and hot inside... now it's confirmed.
This result is a problem for the V2, because to keep it airtight, we need to install piping for water to flow through with a small pump, and have a fan inside the AQUA V2 to allow cooled air to circulate.
Either way, we will need to discuss this.

# July
- [ ] Print and assemble a system that force air flow inside the hulls controlled by radio;
- [ ] Can I measure and see the microcontroller inside temperature on MP?
- [ ] Put the vynil logos

# September
- [ ] Teste fence;
- [ ] smart RTL;
- [ ] Test with a payload of 5 and 10kg;
- [ ] Autonomy with 10 Kg load;
- [ ] Collect videos for AI models
- [ ] Test failsafe situations;
- [ ] Record video with gopro;
- [ ] Measure: see table above
- [ ] Test Failsafe mode!? Radio loss or battery fail: https://ardupilot.org/rover/docs/rover-failsafes.html; Test RTL: Setup -> Mandatory Hardware -> Failsafe: turn off radio and see!?!?
- [ ] Discuss fail safe situations where the boat can continue without connecte to the radio
- [ ] Tests radio and telemetry max distance;
- [ ] Print with obliquo roller printer;

# Future tasks

- [ ] log data procedure;
- [ ] Paint needed or why print in yellow? Filkemp certificate filament LCA
- [ ] Life Cycle Assessment (LCA), including the manufacturing of electronics, wiring and yellow filament production? after service, what should it be used for? ### **Sustainability & Lifecycle**
* **Ando Junior, O. H., et al.** (2022). Experimental Validation of State of Charge Estimation and Lifecycle Analysis. *IEEE Latin America Transactions*, 20(12).
* **Purandare, S., et al.** (2023). Self-Adaptive Mechanisms for Misconfigurations in Small Uncrewed Systems. *SEAMS 2023*, 169-180.
* check this article: services to recycle waste: https://all3dp.com/1/3d-print-recycling-services-guide/?utm_source=newsletter&utm_medium=email&omhide=true
* Contactar esta empresa: https://www.jprior.pt/pt/contacts/ 

- [ ] Review BOM costs;
- [ ] Test guided mode: https://ardupilot.org/rover/docs/guided-mode.html
- [ ] Test in 1 m waves to test the maximum "wake zones" in ports;
- [ ] Review text file business
- [ ] Discuss professional faires;
- [ ] removable protections for corners, bow and stern: how!?!?;
- [ ] Use the radio receptor with 10 CH, with VRA and VRB Flysky Radio
- [ ] What sensors? Think about temperatures, humidity and water sensors inside each hull: we should have an internal temperature sensor, for safety?;
- [ ] Googles and gimball?
- [ ] Plan a test in a testing pull and mechanical resistance laboratory testing?
- [ ] NEXT project phase: decide how to make the avoidance system, by camera using the human control or autonomously by pattern detecting: perhaps both?
- [ ] Ideal diodes for safety when using two bateries and capacitors: https://discuss.ardupilot.org/t/ideal-diodes-when-using-multiple-batteries/75487/62;
- [ ] BMS that can disconnect the bateries from load by radio control;
- [ ] herelink HD video: https://www.cubepilot.com/#/herelink/features
- [ ] Acive radar antenna
- [ ] AIS for boats: https://ardupilot.org/rover/docs/common-ais.html
- [ ] Solar charging proceding and materials?!
- [ ] Packaging
- [ ] Financing
- [ ] (...)

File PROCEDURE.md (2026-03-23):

<!--- ![](Photos/banner-772x250.png --->

# BEFORE
- Fetching the maps with Mission Planner (MP) in a computer with internet access, beforehand;

> NOTE: fetching means, "going" with the MP google map to the location, click with mouse right button and choose the map area with ALT and fetching;

- Check the site permissions to test/use the AQUA;
- Materials check list:
- [ ] computer;
- [ ] trolley;
- [ ] wooden platform to load the AQUA in the vehicle;
- [ ] box (roap; fenders; basic tools; USB cables; aqua battery charger; AA battery charger; AA batteries charged; multimeter charger monitor; telemetry radio; Radio Control transmitter);
- [ ] Mission report

- Available team (ideal four people): radio control, logistics, put and remove the AQUA from water and control of obstacles in the operating environment, computer warnings and data check, and auto mode or guided GPS way points operation;
- Weather forecast: beaufort scale: https://en.wikipedia.org/wiki/Beaufort_scale.
- Check the Radio Control (RC) battery levels;
- AA non-resargeable batteries;
- Charge the AA batteries;
- Charge the AQUA batteries;
- Charge the portable computer batteries (Energy portable computer setup: the automatic shut down should be "never");
- Remember: don't allow the motors to work more then 10s outside the water: they are lubricated only by water!
- binoculars.
- Dinghy boat (if possible).

# DURING OPERATIONS

## PREPARE the MISSION
- Will you include AUTO mode?

> IMPORTANT: where you arm the AQUA will be the RTL return point;

- If AUTO MODE, fix the points in the "Flight plan" screen by clicking with the right mouse button and create sequence points;
- Check the waypoints: are there obstacles between them?
- Auto waypoints vailable option in a grid: there are other advanced options;

## START
- Breefing the team and assign roles: Coordinator; Radio Operator; MP; Logistics, Mooring, and Observation;
- Connect the telemetry radio to the USB C in the computer;
- Turn on the computer and open MP;
- Open the yellow cover ("Open Here") on the starboard float by rotating it;
- Turn on the main power switch: ear the sound similar to a bird saying that the hardware is waiking up;
- Conecting MP to the pixhwack (upper button on the right, on the MP screen): a window appear: wait until the parameters are uploaded;
- Turn on the RC: solid red on the receiver
  
  > hard to see, even if the yellow cover is open;

- In the RC, put the throtle in the middle position;
- Turn on the hardware safety motor switch: two sounds for each motor:

  > it will change from blinking to solid light and emit two tones indicating initialization;

- Check if the telemetry radio transmiter (connected to the computer) has its green led on;
- CHECK the RC radio connection with the CH 5 switch, by cheking if the navigation lights turn on;
- Close the starboard yellow cover by rotating it: main RGB led light BLUE???

## ARM
- Check safety messages: if everything is ok you should see the message "DISARMED";
- Check voltage level: above 14 V;
- Battery above 80%;
- EKF and Vibe white;
- GPS: 3D Fix;
- Check SAT > = 6;
- Check HDOP <2,5;
- Put the boat in the water: if needed use a roap for safety: tie up the boat at the pier;
- Move the boat and see if the compass reacts on the screen;
- Magnetic alignment: align AQUA North south, with the bow to north and the stern to south: degree near 0?

  > IMPORTANT: if not, make a large vehicle magcal and reboot;

- Everything ready to arm the AQUA?
  - Final Security checklist:
    - [ ] no other boats, people or obstacles around AQUA ot in the MP waypoints?
    - [ ] No warning signals on MP;
    - [ ] Radio transmitter control the navigation lights;
    - [ ] AQUA on water
          
- At MP push the ARM/DISARM button: down left window;
- Test the boat response using the RC transmitter;

## RUN
- Untie AQUA
- Drive AQUA mission
- ATTENTION to battery and radio voltage levells and safety screen warnings, namely FAILSAFE, battery levels and telemetry and RC conection
- Monitoring using binoculars: no other boats, people or obstacles around AQUA or between the MP waypoints?
- If you are going to use AUTO mode: change to AUTO by using RC buttons (wright);

## STOP
- Take AQUA to safety shore to RTL or using RTL;
- Tie AQUA;
- DISARM at MP WINDOW;

## RESTART
- untie AQUA;
- ARM at MP;
- Drive AQUA trought the mission goals;

## END
- Bring AQUA to shore
- Disarm at MP window;
- open the yellow starboard float cover
- Turn off motor switch (from solid red led to blink)
- Turn of power;
- Turn off radio control transmitter;
- Disconnect mission planner
- logs!?!?!?!
- continue to fill in the report

# AFTER OPERATIONS
- Clean as much as possible with fresh water: be carefull with the entrances of water above the covers;
- Unscrew the bujons: check for water inside by lifting aqua up to almost the horizontal (60º at least, until 90º);
- collect tools and utensils in the bag and box;
- put everything in the trolley;
- Use the wooden platform to help you get AQUA into the vehicle (if needed);
- Charge AQUA: register capacity values;
- Charge AA radio batteries;
- Conclude the report.

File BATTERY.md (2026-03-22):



# Battery resume and overall FS parameters
AQUA as two bateries packs 4S4P in parallel, meaning that it is a 4S8P setup. Open voltage circuit is 16,7 V with a nominal voltage, 14.4 V (from the manufacturer) and a Cut-off Voltage of 12,0 V (conservative value). Notice that, for each 18650 we have a open circuit voltage of 3.6 V and cutoff 2,65 V, meaning a cutoff around 10.6 V for 4S setup (we use 3V as cutoff voltage). 

 - 4S means, since each 18650 cell as a 3.6 V nominal voltage (manufacturer rate, see: https://batteryservice.bg/wp-content/uploads/2019/11/samsung-35e-e.pdf), we get a whole nominal voltage of **14.4 V** $\ 4 \times 3.6 V \$.
 - 8P means that we add up the individual battery capacity (and energy), we get, since for each battery 2.5 Ah (conservative capacity value), $\8 \times 2.5 Ah \$, meaning 20 Ah for this setup.

So, at a velocity of 1 m/s (3,6 km/h), it has a conservative estimation of 5 hours of autonomy, corresponding to 20 000 mAh capacity and energy available of 288 Wh. The math goes like this:

$/ Energy = Power \times Time = Voltage \times Current \times Time = Voltage \times Capacity \$

Since the nominal voltage is 14.4 V, and the capacity is 20 Ah, so, dividing, we get:

$/ Energy = 14.4 V * 20 Ah = 288 Wh = 0.288 kWh \$

Using the graphs of the technical detail of Bluerobotics (https://bluerobotics.com/store/thrusters/t100-t200-thrusters/t200-thruster-r2-rp/) we can draw some reference operating parameters values.

AQUA as two thusters of 200 W each, capable of handling with 50 A max each. 

Operating at At 1 to 2 m/s velocities (3.6 to 7.2 km/h), current is around 1 to 2 A with voltage around 14.8 to 15.4 V. Each thusrter draws 15 W, so 30 W power in toal, means that at 30 W in total, with an 15.4 measured voltage (Notice that this thrusters have an optimal Operating Voltage between 12 and 16 V).

For these low currents, between 1 to 2 A, with a voltage range between 14 and 16, the PWM is 1360. At this PWM, the thrust is arroun 0.55 to 0.55 Kgf: each motor exerts 500 g, so both, 1 kg; the motors effeciency is really high: from 30.2 to 33.5 g/W (this means that, for each watt of power, we can push 33.5 g: so, if we have 30 W, we get around 1 kg of thrust).

Now, for the autonomy, we go with the max current for both thrusters, 2A, at 2 m/s of max velocity. Since we have 20 Ah, this means that, at a constant current of 2 A we have 10 hours of autonomy.

This are the theoretical values, lets measure it, and confirme the results listed here:

| date |	Velocity (m/s) |	Voltage (V) |	Current (A) | Observations |
|---|---|---|---|---|
| november 2025 | 1.4	| 15.4 	| 1.2 | not really acurate (to be confirmed) |
|  | 	| |  |  |
|  | 	| |  |  |
|  | 	| |  |  |
|  | 	| |  |  |

In conclusion, using the aqua in these conditions of very low velocities, we get the most efficiency regime of T200, in an optimal voltage range, for sure, of 5, but can be up to 6 or even 7 hours of autonomy.

So, for the operacional safety point of view, on MP, we set these parameters:

| Category |	Parameter |	Suggested Value |	Purpose |
|---|---|---|---|
| Monitoring | BATT_MONITOR	| 4	| Activates the monitoring of Voltage and Current|
| Power	| BATT_CAPACITY	| 20000 mAh	| Defines the total capacity for the dual 4S4P (4S8P) pack|
| BATT_LOW_MAH | 4000 |	Triggers alert battery at 20% capacity (4 Ah remaining) |
| Power	| BATT_LOW_VOLT	| 12V |	Should be 12,8V, but we are not conservative here; Safety trigger (3.2V per cell) for voltage-based failsafe, 20% capacity |
| Safety	| BATT_FS_LOW_ACT |	3 (RTL)	| Triggers automatic Return To Launch (Home) on low battery|
| Safety | BATT_FS_CRT_ACT |	3 (RTL)	| RTL in critical situations |
| Navigation	| CRUISE_SPEED |	1.0 m/s	| Nominal mission speed optimized for maximum efficiency|
|Control |	ATC_ACCEL_MAX	| 0.3 m/s²	| Softens acceleration to prevent voltage sag|
| Control | MOT_SLEWRATE |	50 |	Maxim motor change per second (avoid current pics) |
| Auto model, Way Points | WP_RADIUS |	2.0	m | No diretly involve but within the GPS error range in order to use less energy |
| Control | RTL_SPEED |	1.0 m/s |	Return to land in failsafe mode |
| Control | FS_GCS_ENABL |	1	| Not really necessary because we have radio, but it activates RTL if lossing the connection to Mission Planner|
| Control | FS_GCS_TIMEOUT|	60 s | Time of silence before activates the RTL |
| RADIO | FS_THR_ENABLE	| 1 | Enabled RTL protection if radio signal loss |
| RADIO | FS_THR_VALUE |	910	| PWM low value, meaning the system is no longer activated |

And follow this table as a reference to monitor the autonomy of AQUA:

| Voltage | Capacity % | Estimated Capacity | State of Charge |
|---|---|---|---|
| 16.8V | 100% | 20 Ah | Fully Charged (open circuit) |
| 16.0V | 100 % | 20 Ah | High Charge |
| 15.2V | 65% | 12 Ah | Stable Range |
| 14.4V | 50% | 10 Ah | Nominal Voltage |
| 13.6V | 30% | 6 Ah | Low Battery signal |
| 12.8V | 20% | 4 Ah | RTL activated, Critical Level (Failsafe Trigger) |

# DATA and CALCS
Samsung 18650-25R cell capacity and voltage: nominal capacity of 2,500 mAh (2.5 Ah) and a 16,8 V.

==== measure this values ====

AQUA has two BlueRobotics T200 thrusters (https://bluerobotics.com/store/thrusters/t100-t200-thrusters/t200-thruster-r2-rp/). Using this online data its possible to check that, at 1,7 A, we get a 1360 PWM, wich means a measured velocity of 1,5 m/s??? (measured with MP). 

Max Draw: A single T200 can draw up to 25A at full throttle (16V). Two could draw 50A.

1,7 A during and hour, means 1,7 Ah; since AQUA as 20 Ah, then, dividing, we get 11 hours of autonomy. Off course, turnings cost

### Energy Calculation (Wh)
To verify your energy value of 288 Wh, we use the nominal voltage:
$\ Energy (Wh)= 20,000 mAh \times 14.4 V = 288 Wh \$

This sentence uses $\` and \`$ delimiters to show math inline: $`\sqrt{3x-1}+(1+x)^2`$

## 4S4P configuration

---

Compare with this GEMINI title: Battery Voltage and Motor Current

Link: https://gemini.google.com/share/1584391ce280

Aqui tens o documento final consolidado, integrando os objetivos do projeto, a configuração técnica e as referências bibliográficas formatadas.

---

## Bibliographic References

### **Software & Navigation**

* **ArduPilot Dev Team.** (2024). *Rover & Boat Failsafes and Power Monitoring*. ArduPilot Official Documentation. [https://ardupilot.org/rover/docs/rover-failsafes.html](https://ardupilot.org/rover/docs/rover-failsafes.html)
* **Shuck, T.** (2013). *Development of Autonomous Optimal Cooperative Control in Small Unmanned Systems*. AFIT Scholar.

### **Energy & Battery Science**

* **Islam, S. M. R., Park, S. Y., & Balasingam, B.** (2020). Unification of Internal Resistance Estimation Methods for Li-Ion Batteries Using Hysteresis-Free Equivalent Circuit Models. *Batteries*, 6(2), 32. [https://doi.org/10.3390/batteries6020032](https://doi.org/10.3390/batteries6020032)
* **Linden, D., & Reddy, T. B.** (2010). *Handbook of Batteries*. McGraw-Hill Education (4th ed.). [Referência para cálculos de densidade energética e ciclos de vida].
* **Edge, J. S., et al.** (2021). Lithium ion battery degradation: what you need to know. *Physical Chemistry Chemical Physics*, 23(14), 8200-8221.

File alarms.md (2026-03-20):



(Under constructions...)

## SOUNDS AND LED SIGNS

LEDS
https://ardupilot.org/copter/docs/common-leds-pixhawk.html

Safety switch LED meaning¶
Constant blinking - system is initialising
Intermittent blinking - system is ready but in the “Safety” state. press the safety switch to enable output to the motors and control surfaces if already armed, or to cancel the pre-arm error condition that prevents arming.
Solid - safety switch has been pressed, motors and servos are able to move once the vehicle is armed.

https://ardupilot.org/copter/docs/common-safety-switch-pixhawk.html

TONES
https://ardupilot.org/copter/docs/common-sounds-pixhawkpx4.html#common-sounds-pixhawkpx4
https://bluerobotics.com/store/thrusters/speed-controllers/besc30-r3/

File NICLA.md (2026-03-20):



# Nicla Vision

## Sensors/Inputs onboard

- Câmara
- Time-of-flight long distance ranging sensor
- Microfone omnidireccional
- IMU de 6-eixos (*inertial measurment unit*) (3 eixos acelerómetro + 3 eixos giroscópio)

## Comunicação

- USB
- Bluetooth LE
- Wifi

## Questões a resolver

1. Como transmitir vídeo e dados de sensores de forma eficiente para terra
2. Como gravar vídeo e dados para análise posterior
3. Qual o tempo de "streaming" que a bateria aguenta
4. CAN the Nicla Vision charge the battery while on USB?

Location of Nicla Board libraries
~/Library/Arduino15/packages/arduino/hardware/mbed_nicla

## LOG Testes

2026-03-09
¯¯¯¯¯¯¯¯¯¯

Point 4. - Dead Battery today when starting working with Nicla. Measured Voltage
at 0.04V. This is odd.

## Transmit Video and Record Video

**idea**: Setup Nicla with as an Access Point and stream MJPEG. On recording
computer access Niclas Vision Network and record using

### Connect to AP Wifi

Connect to SSID OPENMV_AP with pass 1234567890 or change them in file `aqua_mjpeg_streamer_ap_1.py`

### Play with VLC

File -> Open Network -> `http://192.168.4.1:8080/`

### Record with VLC

In

File -> Open Network -> `http://192.168.4.1:8080/`

activate the option "Stream Output" and use "Settings..." to define output
format/compression.

For monitoring while recording it is best not to activate transcoding.

### Record with ffmpeg

no compression (bigger files)

```sh
ffmpeg -i http://192.168.4.1:8080/ -c copy output.mp4
```

h264 compression (smaller files)

```sh
ffmpeg -i http://192.168.4.1:8080/ -c libx264 output.mp4
```

2026-02-19  
¯¯¯¯¯¯¯¯¯¯

Apesar de funcionar o streaming em formato MJPEG (movie jpeg) é muito lento.
Os melhores resuntados são até o momento:

--- Resoluções

HVGA - 480x320 - transmite a aproximadamente 15 fps.

Resoluções mais altas resultam em erros. Talvez uma solução seja gravar os
vídeos localmente num cartão SD ou num raspberry pi.

2026-02-20  
¯¯¯¯¯¯¯¯¯¯
A experiência com o openMV mostra que:

QVGA 320x240 - Funciona relativamente bem, aprox 25fps
HVGA 480x320 - Funciona mas mais lentamente, aprox 11-15fps
VGA 640x480 - Runtime Error Frame Buffer Overflow
SVGA 800x600 - Runtime Error Frame Buffer Overflow
HD 1280x720 - Runtime Error Frame Buffer Overflow

O problema parece ser que a Nicla Vision não tem memória interna suficiente para
guardar uma imagem maior. Ou seja, apesar do sensor da câmara ser de 2Mp não se
pode utilizar.

Acesso ao servidor AP  
Rede: OPENMV\_AP  
Pass: 1234567890  

XXX (Mudar mais tarde para algo mais personalizado)

Aceder a <http://192.168.4.1:8080/> via Browser ou utilizando o VLC (para gravar
por exemplo, via File-\>Open Network)

### I2C

Scanning I2C bus 1  
No I2C devices found  
Scanning I2C bus 2  
Found devices

- 0x08
- 0x29

Scanning I2C bus 3  
Found devices:

- 0x3C

## SPI

### Battery

MAX17262REWL+T Fuel Gauge

```python
from machine import Pin
for p in dir(Pin.board):
    print(p)
```

A0
A1
A2
CIPO
COPI
CS
D0
D1
D2
D3
DAC1
DAC2
I2C1_SCL
I2C1_SDA
I2C2_SCL
I2C2_SDA
I2C3_SCL
I2C3_SDA
LEDB
LEDG
LEDR
LED_BLUE
LED_GREEN
LED_RED
LPIO0
LPIO1
LPIO2
LPIO3
OSCEN
PA0
PA1
PA10
PA11
PA12
PA13
PA14
PA15
PA2
PA3
PA4
PA5
PA6
PA7
PA8
PA9
PB0
PB1
PB10
PB11
PB12
PB13
PB14
PB15
PB2
PB3
PB4
PB5
PB6
PB7
PB8
PB9
PC0
PC1
PC10
PC11
PC12
PC13
PC14
PC15
PC2
PC3
PC4
PC5
PC6
PC7
PC8
PC9
PD0
PD1
PD10
PD11
PD12
PD13
PD14
PD15
PD2
PD3
PD4
PD5
PD6
PD7
PD8
PD9
PE0
PE1
PE10
PE11
PE12
PE13
PE14
PE15
PE2
PE3
PE4
PE5
PE6
PE7
PE8
PE9
PF0
PF1
PF10
PF11
PF12
PF13
PF14
PF15
PF2
PF3
PF4
PF5
PF6
PF7
PF8
PF9
PG0
PG1
PG10
PG11
PG12
PG13
PG14
PG15
PG2
PG3
PG4
PG5
PG6
PG7
PG8
PG9
PH0
PH1
PH10
PH11
PH12
PH13
PH14
PH15
PH2
PH3
PH4
PH5
PH6
PH7
PH8
PH9
PI0
PI1
PI10
PI11
PI12
PI13
PI14
PI15
PI2
PI3
PI4
PI5
PI6
PI7
PI8
PI9
PJ0
PJ1
PJ10
PJ11
PJ12
PJ13
PJ14
PJ15
PJ2
PJ3
PJ4
PJ5
PJ6
PJ7
PJ8
PJ9
PK0
PK1
PK2
PK3
PK4
PK5
PK6
PK7
SCKL
SCL
SDA
SE05X_EN
UART1_RX
UART1_TX
UART4_RX
UART4_TX
UART6_RX
UART6_TX
UART8_RX
UART8_TX
UART_RX
UART_TX
USB_DM
USB_DP

## References

<https://docs.arduino.cc/resources/pinouts/ABX00051-full-pinout.pdf>
<https://www.analog.com/media/en/technical-documentation/user-guides/max1726x-modelgauge-m5-ez-user-guide.pdf>
<https://www.analog.com/media/en/technical-documentation/user-guides/max1726x-modelgauge-m5-ez-user-guide.pdf>
<https://www.analog.com/media/en/technical-documentation/user-guides/modelgauge-m5-host-side-software-implementation-guide.pdf>

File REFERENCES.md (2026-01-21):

# PLA 
## PLA BEHAVIOR to maritime environments
 - [Behaviour of 3D printed PLA and PLA-PHA in marine environments, G R Montalvão et al 2020 IOP Conf. Ser.: Earth Environ. Sci. 424 012013](https://iopscience.iop.org/article/10.1088/1755-1315/424/1/012013) 
 - [Performance of additively manufactured polylactic acid (PLA) in prolonged marine environments, Polymer Degradation and Stability
Volume 199, May 2022, 109903](https://www.sciencedirect.com/science/article/abs/pii/S0141391022000891)
- [Mechanical Degradation of 3D Printed PLA in Simulated Marine Environment, Surfaces and Interfaces
Volume 21, December 2020, 100778](https://www.sciencedirect.com/science/article/abs/pii/S2468023020307707)
 - [Mechanical Degradation of 3D Printed PLA in Simulated Marine Environment](https://iopscience.iop.org/article/10.1088/1755-1315/424/1/012013)
 - [3D print waterproof](https://makenica.com/how-to-waterproof-your-3d-prints/)

## PLA annealing process
- [Strong 3D prints through ANNEALING, but... Part 1: PLA, CNC Kitchen](https://www.youtube.com/watch?v=dOzVuoBP9gY)
- [Annealing: How to improve your 3D prints, Prusa 3D](https://www.youtube.com/watch?v=6YlGjEY7u38)
- [PLA annealing in a boiling water,My Tech Fun](https://www.youtube.com/watch?v=pRPLtDPoBFE)
- [Annealing efficacy on PLA. Insights on mechanical, thermomechanical and crystallinity characters](https://www.researchgate.net/publication/348668129_Annealing_efficacy_on_PLA_Insights_on_mechanical_thermomechanical_and_crystallinity_characters)

# BIO MATERIALS
- Hart Smart Products, PHA video: [https://www.youtube.com/watch?v=HT4aw-lRMfY](video)
- PHA filament company, behond plastics, https://beyondplastic.com/
- PHA filament company, colorfabb, https://colorfabb.com/

# PRINTING FINISHING
- [How to hide layer lines on 3d prints](https://www.youtube.com/watch?v=xxdjFREJpKs)

# SOFTWARE
(to be updated)
- [Ardupilot Boat configuration](https://ardupilot.org/rover/docs/boat-configuration.html)
- [Configuration parameters example](https://drive.google.com/file/d/17pscxfwTCLuxO1fSMs6sBwvtXfGYWXCk/view?pli=1)
- [Mission Planner boat configurations](https://www.youtube.com/watch?v=PFL-nYuIbuE)

# HARDWARE
- [How to connect a PixHawk Cube or similar system - a simple overview, Painless360](https://www.youtube.com/watch?v=tIE8IN71UFI)
- [PX4 autopilot, Cube Wiring Quick Start ](https://docs.px4.io/main/en/assembly/quick_start_cube.html#rc_control)
- [Ardupilot Receiver](https://ardupilot.org/copter/docs/common-rc-systems.html)
- [Pixwack pro wiring](https://docs.px4.io/main/en/assembly/quick_start_pixhawk.html)
- [Pixhawk connector diagram](https://ardupilot.org/copter/docs/common-pixhawk-overview.html)
- [Radio telemetry, Atlatl/HV](https://www.youtube.com/watch?v=4xW_c2qP68c)
- [CONECTORS](https://www.mattmillman.com/info/crimpconnectors/common-jst-connector-types/)
- [Thruster User Guide](https://bluerobotics.com/learn/thruster-usage-guide/)
- [T200](https://bluerobotics.com/learn/thruster-usage-guide/)
- [Minimum Throttle, dead zone](https://ardupilot.org/rover/docs/rover-motor-and-servo-configuration.html#rover-motor-and-servo-min-throttle)
  
# Radio Transmitter
- [Binding and Setting Up the FlySky i6 Transmitter for a quadcopter/drone](https://www.youtube.com/watch?v=9-Z0rTVEkHI)

# Telemetry
- [Holybro Telemetry Radio]([https://www.youtube.com/watch?v=9-Z0rTVEkHI](https://docs.px4.io/main/en/telemetry/holybro_sik_radio.html))

# AVOIDANCE
- [Radar based collision detection developments on USV ROAZ II, June 2009, SourceIEEE Xplore](https://www.researchgate.net/publication/224599932_Radar_based_collision_detection_developments_on_USV_ROAZ_II)

# LAW
- [Princípios de Conduta da Indústria de Navios de Superfície Autônomos Marítimos e Código de Prática versão 4](https://www.maritimeuk.org/media-centre/publications/maritime-autonomous-surface-ships-industry-conduct-principles-code-practice-v4/)

# SONAR
- [Mapping The Floor of Ladybird Lake, Clay P. McPherson](https://www.clay-p-mcpherson.com/projects/mapping-the-floor-of-ladybird-lake)

# OSD
- [FPV, Holybro micro OSD v2](https://www.youtube.com/watch?v=ghhqSGxdIwQ&t=421s)
- [FPV, Holybro micro OSD v2 wiring](https://www.flyingtech.co.uk/wp-content/uploads/2021/03/HolyBro-Micro-OSD-V2-Manual-with-HolyBro-formatting-v0.1-copy.pdf)

# OTHER PROJECTS
- [My Autonomous Sonar Boat, Red Maniac RC](https://www.youtube.com/watch?v=G87lRPbBeAo&t=5s)
- [Autonomous Box Boat - Long Range Waypoint Mission,rctestflight ](https://www.youtube.com/watch?v=PlUmG3CFadw)
- [Infinite Range Autonomous GPS Boat, Clay Builds](https://www.youtube.com/watch?v=zQqv1K1cKas)
- [Insanely High Tech Autonomous sonar depth survey Rc Boat assisted by Oxidean Marine!, Bill Oxidean ](https://www.youtube.com/watch?v=59jIy3ck_OY)
- [3D Printed RC Utility Boat - Hull and Drive System - Part 1, electrosync](https://www.youtube.com/watch?v=0KblE-0bh7o)
- [Arduino Sonar Boat, Clay P. McPherson](https://github.com/ClayBuilds/Gumption-Trap-)
- [ Boat build part 2 - Preparing the autopilot, The Carp Pilot ](https://www.youtube.com/watch?v=PFL-nYuIbuE)
- [MIT deploys first full-scale autonomous Roboat on canals of Amsterdam](https://newatlas.com/marine/mit-first-full-scale-autonomous-roboat-amsterdam/)
- [Robot Boats Survive Epic Voyage Across the Pacific — So Far](https://www.wired.com/2012/05/wave-glider-crosses-pacific/)
- [Aquatic Drones Builds Data Service for Europe and Beyond](https://www.therobotreport.com/aquatic-drones-builds-data-service-for-europe-and-beyond/)

# EXAMPLES OF AUTONOMOUS BOATS
- [Further Testing of Materials for Radio Controlled Yachts](https://3dprintedradioyachts.com/testing-materials-radio-controlled-yachts/)
- [How to 3D print a boat](https://arcticchallenge.co.uk/2022/03/13/how-to-3d-print-a-boat/)
- [3D Printed Boats: Everything You Need to Know](https://www.nikkoindustries.com/blogs/news/3d-printed-boats-everything-you-need-to-know)
- [A New Approach to 3D Printing a Yacht Hull Mold](https://blog.thermwood.com/en-us/a-new-approach-to-3d-printing-a-yacht-hull-mold)
- [AUTONOMOUS solar boats, crossing the atlantic](https://www.youtube.com/watch?v=R3e2wp8KGQs)

# USV's (Unmanned Surface Vessels)
- [wikipedia](https://en.wikipedia.org/wiki/Unmanned_surface_vehicle)
- [Unmanned Surface Vehicles, 15 Years of Development, Justin E. Manley, Battelle Applied Coastal and Environmental Services
3, http://www.battelle.org](https://www.ieeeoes.org/history/080515-175.pdf)

# LEARNING
- [DRONE BOT workshop](https://dronebotworkshop.com/)
- [ARDU PILOT](https://ardupilot.org/ardupilot/)
- [Painless360](https://www.youtube.com/@Painless360)
- [Opensource Drone](https://www.youtube.com/watch?v=QvRxxjaLjxg)

# RESEARCH INSTITUTES

# FAIRES

# PROFESSIONAL COMPANIES 
- [ORCA](https://expresso.pt/sociedade/ciencia/2022-03-24-ORCA.-O-barco-autonomo-que-promete-levar-o-CEIIA-a-novos-negocios-6b455650)
- [BlueBoat](https://bluerobotics.com/product-category/boat/)
- [Sea Floor Systems](https://www.seafloorsystems.com)
- [Saildrone](https://www.saildrone.com/technology/vehicles)
- [Multi-Purpose Unmanned Surface Vehicle 4.0, Submergence Group & Affiliates ](https://www.youtube.com/watch?v=szRWuguDHuo)
- [UNIQUE GROUP](https://www.uniquegroup.com/solutions/unmanned-survey-vessels/?utm_source=google&utm_medium=cpc&utm_campaign=usv-western-hemisphere-search&utm_term=auv%20systems&utm_content=generic-asv&utm_term=auv%20systems&utm_campaign=ASV++(fixed+530)&utm_source=adwords&utm_medium=ppc&hsa_acc=8945981504&hsa_cam=18151076352&hsa_grp=146223606371&hsa_ad=618282513483&hsa_src=g&hsa_tgt=kwd-1956749695874&hsa_kw=auv%20systems&hsa_mt=p&hsa_net=adwords&hsa_ver=3&gad_source=1&gclid=CjwKCAjwrvyxBhAbEiwAEg_Kgldm15CWGCjYWvxruiFVsk_4542mwJyCSkMrPS3XFkaD6jwo1U3cahoCkJMQAvD_BwE)
- [Seasats](https://seasats.com/)

# EPOXY
- https://bramptontechnology.com/understanding-the-science-of-waterproof-epoxy/?srsltid=AfmBOooUiCUlK0Fa6sgTrG4pshEND0tu8YvJhRhPGMW3OeZWKQ4ipXv1
- https://www.reallandcomposite.com/How-Marine-Resin-and-Regular-Epoxy-Perform-in-Boat-Repairs-2025-Guide.html
- https://www.mdpi.com/2073-4360/16/11/1510
- https://www.sciencedirect.com/science/article/pii/S259012302401034X

# LORA
- [You’ve Never Seen WiFi Like This, Data Slayer](https://www.youtube.com/watch?v=9azEfCQNhSA)

# Nicla Vision
- Nicla Vision Tutorial, https://github.com/sixhat/Nicla-Vision-Tutorial-4h/tree/main

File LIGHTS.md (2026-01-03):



This is not completed...

Using a pixwack pin to control sommething with the radio channels, like a light or a gimball, there are two things you must know in advance:

1. There are two groups of pins, MAIN and AUX;
2. And, if you are using a SAFETY SWITCH, you must turn it on to test because, pixwack only activate those pins when it's on.

Its very easy: after version ardurover 4.2, you have to assign the SERVOx_function to a RCINx channel, just that!!! x is the channel/pin you want to use.

Material you need: a driver (mosfet) powered not by the pixwack, because it doesn't accept high currents;

STEPS

Connect Your Receiver: Ensure your RC receiver is correctly connected to the Pixhawk. 
Open Ground Control Software: Launch Mission Planner (for ArduPilot) or QGroundControl (for PX4). 
Access Parameter List: Navigate to the full parameter list or tree. 
Find Servo Parameters: Locate the SERVOx_FUNCTION parameter that corresponds to the AUX output you want to use; example: SERVO9_FUNCTION for AUX output 9). 
Assign RC Input Channel: Use the RCx_FUNCTION parameter (e.g., RC9_FUNCTION) to assign the input RC channel that will control this function. 

Important Considerations

    Low Current Bus:
    The AUX outputs are on a low-current bus, so it's best to power servos from a separate alternate source to avoid overloading it.

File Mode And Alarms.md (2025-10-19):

update about this...
- Operation mode: NORMAL or SIMPLE or AUTO? (WICH BUTTONS!?!?!?)
https://ardupilot.org/rover/docs/boat-configuration.html
- Types of ArduBoat driving modes

    Autonomous Modes:
        Auto: Follows a pre-programmed mission, often from a ground station.
        Guided: Follows a specific command from the ground station, like moving to a new waypoint.
    Position-Holding Modes:
        Loiter: Holds the boat in its current position, even after it reaches a destination.
        PosHold: Holds the vehicle's current position in altitude and location.
    Return/Landing Modes:
        RTL (Return-to-Launch): Commands the boat to return to its starting point.
        SmartRTL: A variation of RTL that attempts to maintain position after reaching the destination.
        Land: Commands the boat to land at its current location.
    Manual/Assisted Control Modes:
        Manual: The pilot has direct control over the vehicle's motors and movement.
        Acro: Requires pilot input to hold heading and roll, with no automatic stabilization.
        Stabilize: A form of assisted control where the vehicle self-levels its attitude when the control sticks are released.
- In the case of AUTO, ways point settled??? https://ardupilot.org/planner/docs/common-mission-planning.html

### SOUNDS AND LED SIGNS

LEDS
https://ardupilot.org/copter/docs/common-leds-pixhawk.html

Safety switch LED meaning¶
Constant blinking - system is initialising
Intermittent blinking - system is ready but in the “Safety” state. press the safety switch to enable output to the motors and control surfaces if already armed, or to cancel the pre-arm error condition that prevents arming.
Solid - safety switch has been pressed, motors and servos are able to move once the vehicle is armed.

https://ardupilot.org/copter/docs/common-safety-switch-pixhawk.html

TONES
https://ardupilot.org/copter/docs/common-sounds-pixhawkpx4.html#common-sounds-pixhawkpx4
https://bluerobotics.com/store/thrusters/speed-controllers/besc30-r3/

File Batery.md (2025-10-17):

Safety issues. This a GEMINI text to the question why the safety switch is giveing a a warning and the batery is  full...!?!?!?

This is a very common issue with Pixhawk (ArduPilot or PX4 firmware) systems! The low battery warning is usually triggered based on **voltage** and/or **remaining capacity** thresholds configured in the flight controller, and if those settings are incorrect, you can get a false alarm even with a fully charged battery.

Here are the most likely causes and what you should check:

### 1. Incorrect Battery Monitor Calibration (Most Common)

The Power Module (or "Power Brick") connected to the Pixhawk measures the battery voltage and current. If the internal scaling factor is wrong, the flight controller will read an incorrect, usually lower, voltage.

**What to check and how to fix it:**

* **Check the Voltage Reading:** Connect your Pixhawk to a Ground Control Station (GCS) like **Mission Planner (for ArduPilot)** or **QGroundControl (for PX4)**. Look at the live battery voltage reading.
* **Measure the True Voltage:** Use a **multimeter** to measure the voltage directly at your battery's connector.
* **Compare and Calibrate:** If the GCS voltage is significantly lower than the multimeter voltage, you need to calibrate the Power Module's voltage divider ratio.
    * **In Mission Planner (ArduPilot):** Go to **Initial Setup > Optional Hardware > Battery Monitor** (or **Setup > Battery Monitor**). You'll typically be asked to enter the measured voltage (from your multimeter) next to the displayed voltage (from the GCS). The software will calculate the correct **Voltage Divider** value.
    * **In QGroundControl (PX4):** Go to **Vehicle Setup > Power** and check/correct the **Voltage Divider** setting.

* *Example of a common error:* One user reported their Pixhawk Power Module was reading $2 \text{V}$ below the actual voltage, which was fixed by performing the proper calibration.

### 2. Incorrect Low Voltage Thresholds

The Pixhawk has parameters that define what constitutes a "low" or "critical" battery level, either by a minimum **voltage** or minimum **remaining capacity (mAh)**. If these thresholds are set too high for your specific battery, the alarm will trigger too early.

**What to check and how to fix it (for ArduPilot/Mission Planner):**

Look at these parameters and adjust them if necessary (or check the corresponding settings in QGroundControl):

* **`BATT_LOW_VOLT`:** The voltage level (per cell or total, depending on the parameter) that triggers the **low** action (usually a warning or Return-To-Launch/Home (RTL)).
* **`BATT_CRT_VOLT`:** The voltage level that triggers the **critical** action (usually an immediate Land).
* **`BATT_LOW_MAH` / `BATT_CRT_MAH`:** The remaining battery capacity (in mAh) that triggers the low/critical actions.

**Typical LiPo guidelines:**
* A fully charged LiPo cell is $4.2 \text{V}$.
* The voltage alarm is usually set around **$3.5 \text{V}$ to $3.7 \text{V}$ per cell** under *load*.
* For a fully charged $3\text{S}$ battery ($\sim 12.6 \text{V}$), an incorrect alarm may trigger if a low voltage like $11.1 \text{V}$ is set too high or the voltage reading is off (see point 1).

### 3. Incorrect Battery Capacity Parameter

The flight controller uses the defined battery capacity to estimate the remaining percentage. If the set capacity is **too low** (e.g., set to $3000 \text{mAh}$ for a $5000 \text{mAh}$ battery), the estimated remaining capacity will drop quickly, triggering the capacity-based low battery warning prematurely.

**What to check and how to fix it (for ArduPilot/Mission Planner):**

* **`BATT_CAPACITY`:** Ensure this parameter is set to the correct rated capacity (in mAh) of your battery.

### 4. Poor Physical Connections

A loose or damaged connection between the battery, the Power Module, and the Pixhawk can cause a momentary or continuous **voltage drop** which the flight controller interprets as a low battery.

**What to check:**

* **Inspect all cables** for wear or damage.
* **Ensure the Power Module connector** is fully and firmly seated on the Pixhawk.
* **Check the main battery connector** for corrosion or a poor fit.

### 5. Faulty Power Module or Pixhawk

If you have tried calibration and checked the parameters without success, the Power Module itself might be faulty and reading the voltage incorrectly, or there could be an issue with the voltage sensing circuitry on the Pixhawk.

**What to try:**

* **Check the $5 \text{V}$ rail:** Some issues are related to the $5 \text{V}$ power supplied by the Power Module's BEC. Use a multimeter to measure the $5 \text{V}$ pins on the Power Module connector to ensure they are stable and near $5.3 \text{V}$ (as suggested in some forums).
* **Try a different Power Module or Battery:** If possible, swap the Power Module or use another known-good battery to see if the problem persists.

**In summary, the most immediate steps are:**

1.  **Check the live voltage reading** in your GCS (Mission Planner/QGroundControl).
2.  **Measure the battery voltage** with a multimeter.
3.  **Calibrate the Battery Monitor** in your GCS if the readings do not match.
4.  **Verify the `BATT_LOW_VOLT` and `BATT_CAPACITY`** parameters are correctly set for your battery.

Monitoring and calibration BATT_MONITOR: Selects the battery monitoring type. Common values are \(3\) for voltage-only and \(4\) for both voltage and current.BATT_VOLT_PIN: Specifies the autopilot's analog pin connected to the power module's voltage sensing output.BATT_CURR_PIN: Specifies the autopilot's analog pin connected to the power module's current sensing output.BATT_VOLT_MULT: Scales the raw voltage reading from the sensor to get the actual battery voltage.BATT_AMP_PERVLT: Converts the voltage reading from the current sensor into a current reading in amps.BATT_AMP_OFFSET: Adjusts for any voltage offset from the current sensor when no current is being drawn.BATT_CURR_MULT: Scales reported current values for specific monitors like DroneCAN. Failsafe and safety BATT_LOW_VOLT: The voltage threshold for the "low battery" warning and action.BATT_CRT_VOLT: The voltage threshold for the "critical battery" warning and action. Set to zero to disable.BATT_LOW_MAH: The remaining capacity in mAh for the "low battery" failsafe.BATT_CRT_MAH: The remaining capacity in mAh for the "critical battery" failsafe.BATT_FS_LOW_ACT: The action to take when the low battery threshold is reached, such as "RTL" (Return to Launch) or "Land".BATT_FS_CRT_ACT: The action to take when the critical battery threshold is reached.BATT_ARM_VOLT: The minimum voltage required to arm the vehicle.BATT_ARM_MAH: The minimum remaining capacity in mAh required to arm the vehicle. Other parameters BATT_CAPACITY: Automatically updated to the battery's actual capacity in mAh after it's been used.BATT_SERIAL_NUM: Used for SMBus or DroneCAN monitors to identify which battery it is monitoring.BATT_MAX_AMPS: The maximum current to be reported, primarily for INA2xx sensors.

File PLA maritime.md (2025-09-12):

## About PLA in maritime environments

NOTE: This text was created by GEMINI AI, using this text "turning a PLA as a material to use in boats and maritime platforms", and edited afterwards by the author's:

Turning PLA into material for boats is a complex process due to PLA's susceptibility to **moisture absorption** and **degradation** in marine environments, but advancements in PLA-PHA composites and incorporating waste materials offer potential for maritime applications, such as marine debris reuse or high-performance composites, although it requires further study and development for practical and durable boat components. 
Understanding the Challenges of PLA in Marine Environments

## Potential Solutions and Emerging Applications

1. PLA-PHA Composites: 
Combining PLA with Polyhydroxyalkanoates (PHA) can improve the material's performance in marine environments by offering a balance of biodegradability and better mechanical properties. 

2. Marine Waste as a Resource:
Researchers are exploring the use of marine plastic waste as a source material to create new filaments for 3D printing, offering a sustainable solution for both pollution reduction and material sourcing in the maritime sector. 

3. Green Composites:
Incorporating agricultural or marine waste into PLA to form green composites can reduce costs and enhance biodegradability without significantly compromising mechanical performance. 

## Current Research and Future Prospects

1. Accelerated Aging Models:
Studies are developing models to predict the lifespan of 3D printed PLA components under marine conditions, a crucial step for understanding their long-term viability. 

2. Mechanical Degradation Studies:
The behavior of 3D printed PLA in simulated seawater environments is being studied to identify mechanical weaknesses, such as a decrease in ductility and yield strength, and to understand the effects of environmental factors on its performance. 

3. Sustainable Manufacturing:
3D printing is being recognized as a promising tool for cleaner production in the maritime industry, with the potential to produce components from recycled and bio-based materials. 

## Glossary

Moisture Absorption:
PLA's ability to absorb water can lead to swelling and embrittlement, reducing its mechanical strength and lifespan in marine conditions. 

Biodegradation:
While its eco-friendly nature is an advantage, PLA's potential to biodegrade too quickly in seawater can make it unsuitable for long-term use in maritime structures. 

## References

https://www.sciencedirect.com/science/article/abs/pii/S0141391022000891

https://iopscience.iop.org/article/10.1088/1755-1315/424/1/012013 (https://iopscience.iop.org/article/10.1088/1755-1315/424/1/012013/pdf) 

https://www.mdpi.com/2073-4360/13/9/1361

https://www.sciencedirect.com/science/article/pii/S0959652623013094

https://www.mdpi.com/2073-4360/11/3/400#:~:text=Nonetheless%2C%20when%20blended%20with%20PLA%2C%20it%20(,enhanced%20physical%20properties%20and%20processability%20%5B%2017%5D.

https://www.sciencedirect.com/science/article/pii/S2772416625001688#:~:text=Furthermore%2C%20blending%20PLA%20with%20other%20bio%2Dbased%20materials%2C,applications%20(%20Boz%C3%B3%20et%20al.%2C%202021)%20.

https://addi.ehu.es/handle/10810/60371

This was not from AI:
https://www.ifam.fraunhofer.de/en/Press_Releases/biodegradable-antifouling-coatings.html

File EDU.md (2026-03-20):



The idea of building a small catamaran as an educational project to teach robotics and engineering is exceptionally valid and full of potential. 
Here's a detailed analysis, with specific nuances for the Portuguese context:

Project Advantages:

    Practical and Engaging Learning:
        This project provides a practical and dynamic experience, allowing students to apply theoretical robotics and engineering concepts in a real-world scenario.
        Students can acquire knowledge in design, construction, electronics, programming and mechanics, all integrated into a single project.
    Multidisciplinarity:
        The project covers several areas of knowledge, such as physics (hydrodynamics, stability), maths (design calculations, geometry), electronics (sensors, actuators) and programming (control of the catamaran).
        This fosters the development of transversal competences and an understanding of the interconnection between different disciplines.
    Development of Essential Skills:
        The project stimulates the development of crucial skills such as problem-solving, teamwork, critical thinking and creativity.
        Students learn to plan, design, build, test and optimise the catamaran, facing challenges and finding innovative solutions.
    Motivation and interest:
        Building a catamaran is a stimulating and motivating project, capable of arousing students' interest in robotics and engineering.
        The possibility of seeing the catamaran sailing and working is a rewarding experience for the students.

Important Considerations in the Portuguese Context:

    Adjusted Complexity:
        It is essential to adapt the complexity of the project to the level of knowledge of the students, taking into account the Portuguese school curricula.
        For beginners, you could start with a simple catamaran, with basic functions, and gradually add more advanced features.
    Safety First:
        Safety must be a priority at every stage of the project, especially in Portugal, where safety regulations are strict.
        It's crucial to provide students with the necessary personal protective equipment and to supervise construction and testing activities.
    Resources and Partnerships:
        Building a catamaran requires material and financial resources.
        It is important to seek partnerships with local companies, universities and research centres to obtain technical and financial support.
    Utilising the coastline:
        Portugal has a vast coastline, which makes this type of project particularly relevant.
        The use of renewable energies, such as solar energy, to power the catamaran can be explored, in line with current environmental concerns.

Exploration possibilities:

    Advanced Robotics:
        Implement sophisticated automatic control systems, such as autonomous navigation with GPS, speed control and steering with artificial intelligence.
        Use sensors to collect environmental data relevant to Portugal, such as water temperature, salinity and wave strength.
    Cutting-edge engineering:
        Explore different hull designs and propulsion systems to optimise the catamaran's performance in Portuguese waters.
        Using composite materials and advanced manufacturing techniques, such as 3D printing, to build the catamaran.

In short, the construction of a small catamaran is a valuable educational project suited to the Portuguese context, which can provide a rich and meaningful learning experience for students, while promoting the development of essential skills for the future.

Disclaimer: adapted from AI GEMINI.

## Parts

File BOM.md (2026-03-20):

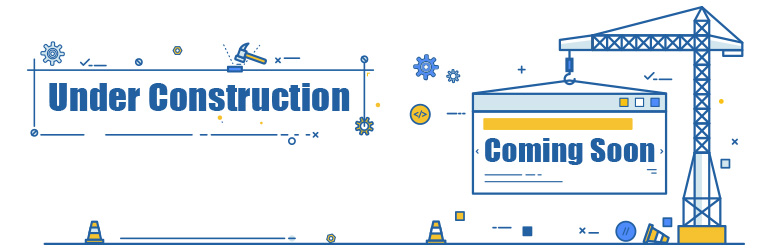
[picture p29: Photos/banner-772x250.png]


This is a list of materials and working time, used in this project. However, its still an approximation, but a good one. There are consumables that were bougth more then necessary but in a wholesail that's what usual happen. The total amount is 8446,42 euros. At the same we reconstruct the aqua version bodyboard. The working time was supported by David, Nuno and António.

# BOM resume

| Area  | AMOUNT | cost (euros)| Remarks |
| ------------- | ------------- | ------------- | ------------- |
| Working time  | 455 h | 9100 |  | 
| Materials and consumables  | | 3085,75 ||
| Tools |  | 420 ||
| Hardware |  | 1380,67 ||
| Total | | | 13986,42 |

# Working time

| Title  | desciption | #  |cost (euros)| Remarks |
| ------------- | ------------- | ------------- | ------------- | ------------- |
| Working time  | May and June 2024 | 48 hours  | 960 |Hardware mounting and catamaran testing | 
| Working time  | 2019 - 2023 | 120 hours  | 2400 | Non-functional prototype |
| Working time  | January 2024 | 20 hours  | 400| Preparing the Hulls | 
| Working time  | February 2024 | 16 hours  | 320| Glueing and sanding |
| Working time  | March 2024 | 24 hours  | 480 |Sanding and Painting |
| Working time  | April 2024 | 24 hours  | 480 |Painting| 
| Working time  | May and June 2024 | 48 hours  | 960 |Hardware mounting and catamaran testing |
| Working time  | October and November 2024 | 35 hours  | 700 |Hardware mounting and catamaran testing | 
| Working time  | Jannuary throught December 2025 | 120 hours  | 2400 |Hardware mounting and catamaran testing | 

# Consumables and materials

| Title  | description | #  |cost (euros)| Remarks |
| ------------- | ------------- | ------------- | ------------- | ------------- |
| 3D printing  | February 2024 | 15 days  | 2500 | Printing the Hulls sponsored by MAUSER.pt | 
| Polyester Plamuur | March 2024 | 1  | 54 | Preparing the surface | 
| Painting materials  | Airo-chemie AIRO PRIMEFILL | 4  | 65 | Primer |
| Painting materials  | Chemitool chemisol acrylic paint | 8 | 42 |  |
| ACRYLIC VARNISH | mtm spray 400 mL | 4 | 38,15 | |
| Glue | BLOK universal (Vinyl Acetate) | 10 | 63 |Preparing the Hulls |
| Security | Gloves, glasses and power tool respirator | 1 | 65 |  |
| Hardener and resin | Entropy Resin ER-CLR 5 Kg and hardener 2.15 Kg, Pasteur pipettes, color tints |1|262 ||
| Workshop space | 12 months | 12 | 2880 | Sponsored by Marçal Metalonecânica |
| Tapes |Powerbond, double sided tape, terminals, heat shrink| 53 |||

# Tools

| Title  | description | #  |cost (euros)| Remarks |
| ------------- | ------------- | ------------- | ------------- | ------------- |
| Mask | 3M™ Particulate Respirator, FFP2, Valved, 8822 | 6 | 25 |  |
| Mask | Field 0503002 CE0181, www.cls.pt | 1 | 42 |  |
| Mask | Delta Plus M6400 MARS KIT | 1 | 23 |  |
| gloves | gloves | 100 | 8 | |
| sandpaper| Grit 200 to 1500 | 25 | 22 | |
| Portable Computer | Lenovo ThinkPad | 1 | 300 |  |
| Crimpºing tool | 1 | 12,99 ||
| Precision scredriver set | 1 | 10,99 ||
| Soldering support | | 1 | 18 ||

# "Hardware"

| Title  | description | #  |cost (euros)| Remarks |
| ------------- | ------------- | ------------- | ------------- | ------------- |
| PIXWACK 2 | OFFICIAL | 1 | 230 |  |
| Pixhawk PX4 PRO | Pixhawk2.4.8 32bit Flight Controller Autopilot TYPE-C/ USB Port Futaba SBUS M8N GPS 3DR Radio V5 Telemetry DIY | 1 | 164 |  |
| F4V3S | Flight Controller Board | 1 | 34 |  |
| DC MOTORS | AIDNTBEO Underwater Thruster | 2 | 55 |  |
| DC MOTORS | Blue robotics Thruster 100 W | 2 | 255 |  |
| DC MOTORS | Blue robotics Thruster 200 W | 2 | 476 |  |
| Video Transmission | Skydroid Hsthe Sea Receptor FPV | 1 | 36,58 |  |
| Video Transmission | Holybro micro osd v2 | 1 | 28,09 |  |
| Video Transmission | Agatige Antena De 5,8 GHz, 3Dbi RHCP | 2 | 14 |  |
| Camera onBoard | mini Camera HD | 1 | 24 |  |
| Video trasmission | OSD Holybro | 1 | 27 |  |
| Radio Transmission | ??? | 1 | 53 |  |

# Spare parts

| Title  | description | #  |cost (euros)| Remarks |
| ------------- | ------------- | ------------- | ------------- | ------------- |
| Pixwack 4 flight controller |  | 1 | 113 |  |
| Holybro mini OSB |  | 1 | 32 |  |

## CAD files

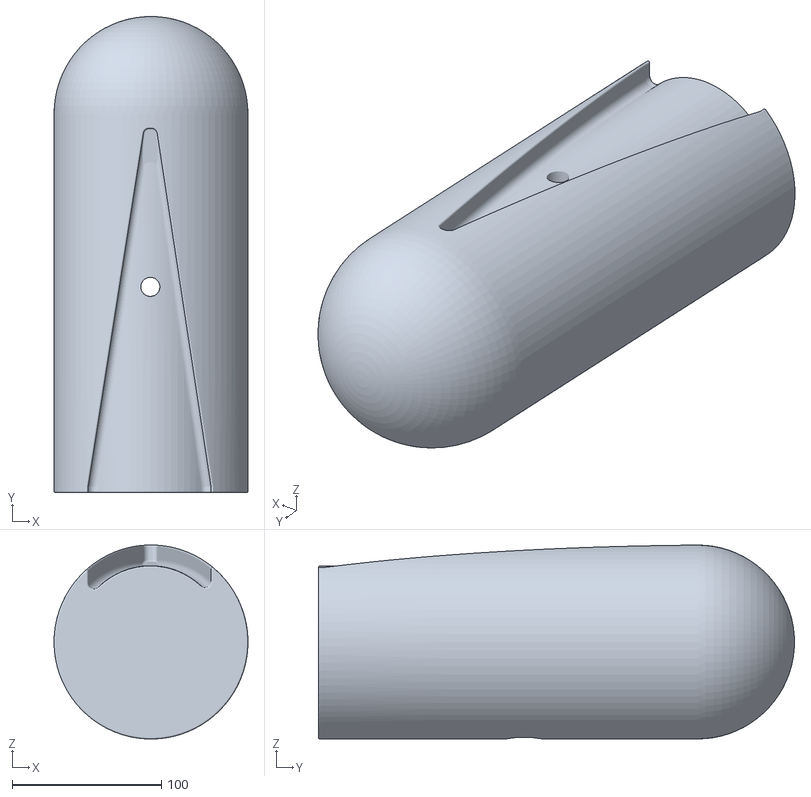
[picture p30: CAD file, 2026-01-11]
3D/flutuadorProa.stl
130.0 x 319.0 x 130.0

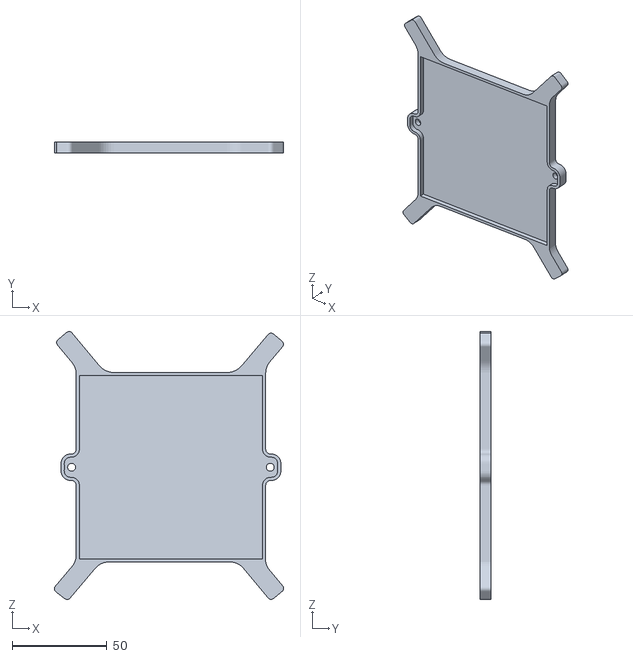
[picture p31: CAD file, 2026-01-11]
3D/tampa.stl
121.0 x 6.00 x 141.4

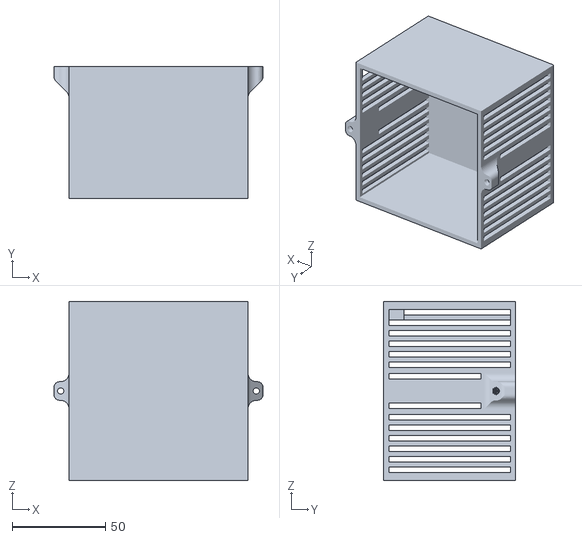
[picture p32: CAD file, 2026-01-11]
3D/cx.stl
112.0 x 71.0 x 96.0

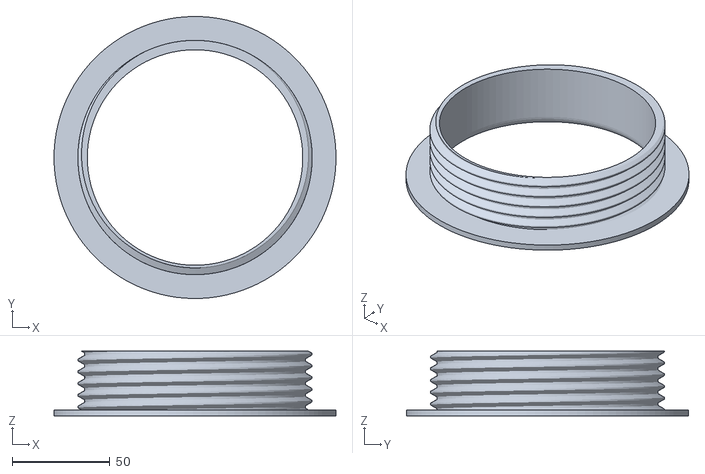
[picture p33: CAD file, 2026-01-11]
3D/TampaInterior.stl
144.0 x 144.0 x 33.0

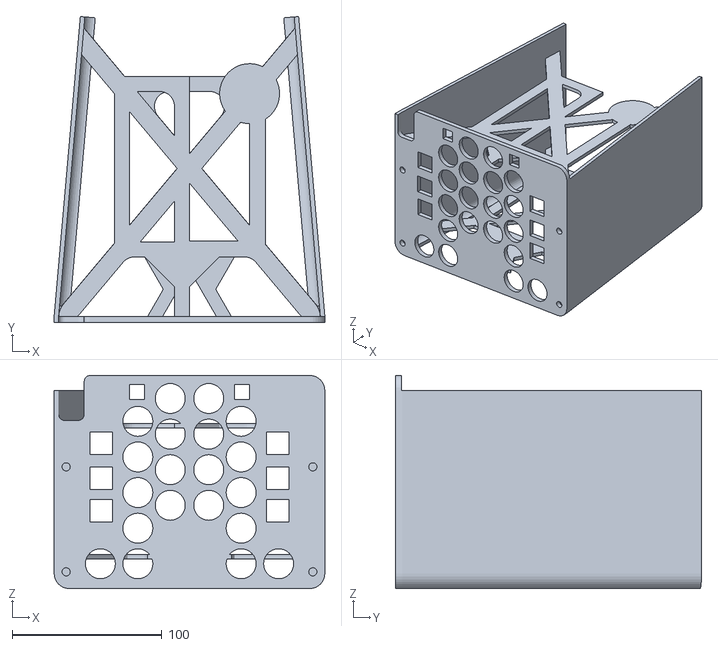
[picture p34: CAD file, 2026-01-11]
3D/CxHardware.stl
180.6 x 204.1 x 142.1

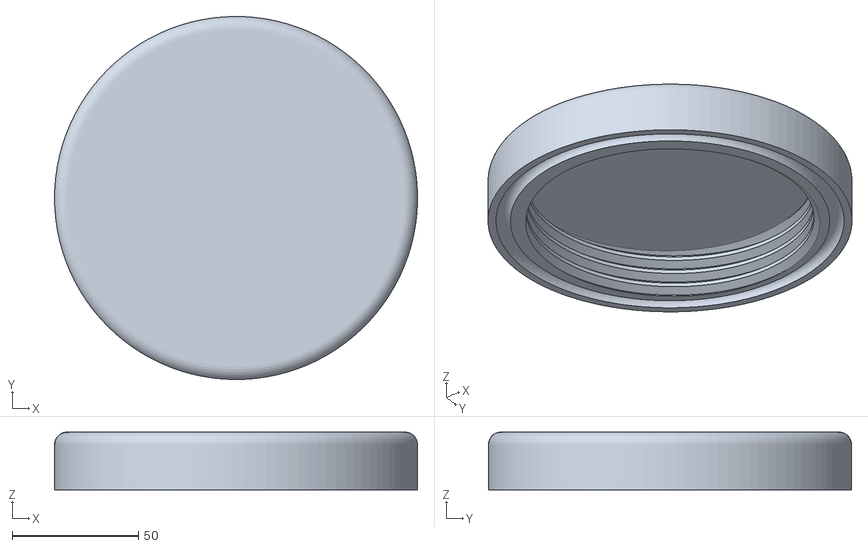
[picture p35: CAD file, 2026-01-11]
3D/tampaExterior.stl
144.0 x 144.0 x 23.0

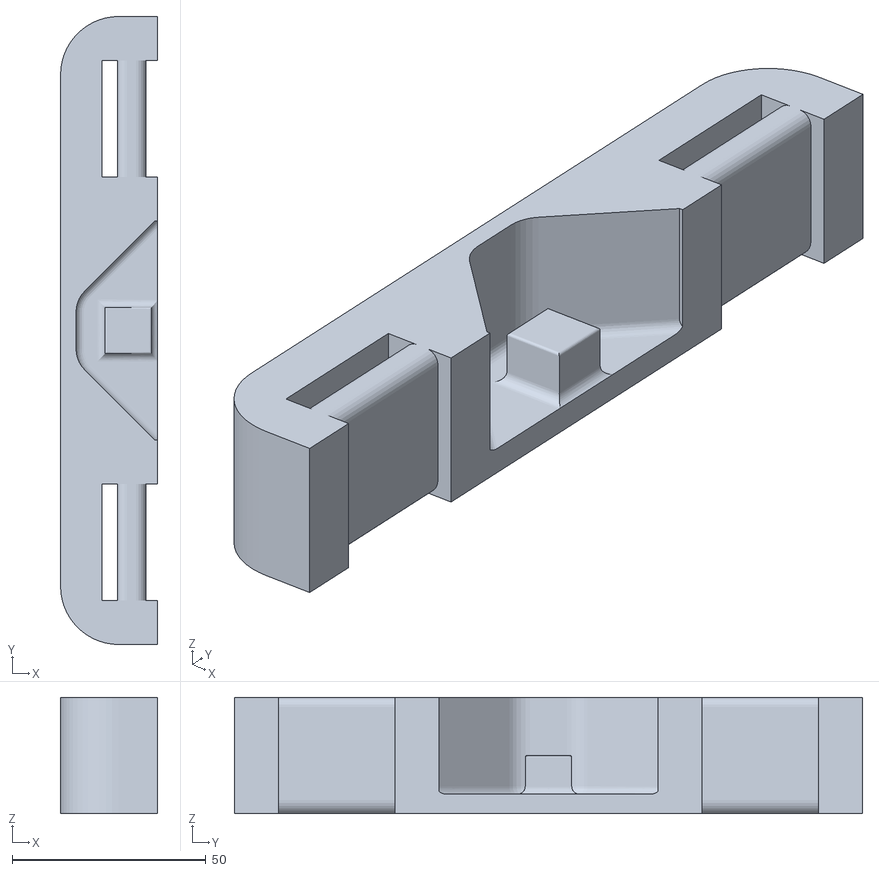
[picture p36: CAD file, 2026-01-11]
3D/SuporteCinta.stl
25.0 x 162.1 x 30.0

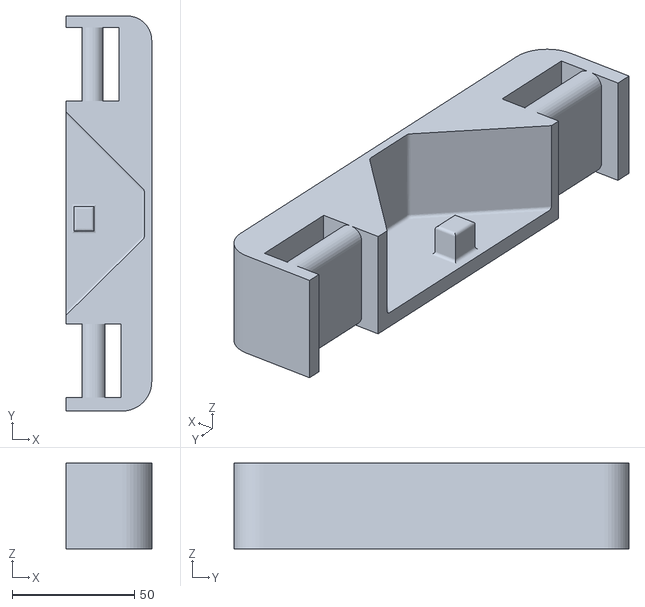
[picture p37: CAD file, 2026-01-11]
3D/SuporteCinta2.stl
35.0 x 161.6 x 35.0

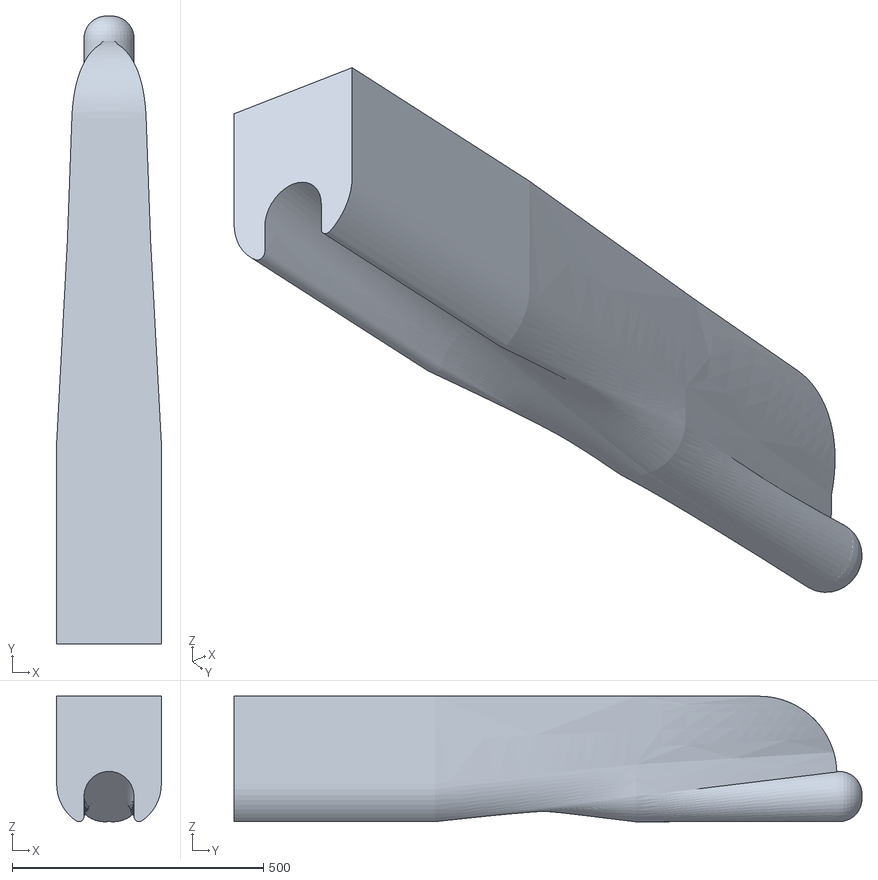
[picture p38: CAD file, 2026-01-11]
3D/estibordo_V9.stl
208.5 x 1250.0 x 250.4

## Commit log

2024-03-08 Create BOM
    starting th BOM materials
2024-05-25 Update README.md
    wiring
2024-09-22 julho2024
    fotos de julho de 2024
2025-10-16 Revise AQUA operation procedure and safety checks
    Updated the procedure for operating the AQUA, including material checks, operational modes, and safety procedures.
2025-10-17 Revise JOURNAL.md with latest updates and fixes
    Updated the journal with recent progress and issues encountered during testing and assembly.
2025-10-17 Document battery safety warning troubleshooting steps
    Added a detailed guide on troubleshooting battery safety warnings for Pixhawk systems, covering calibration, voltage thresholds, capacity parameters, connections, and potential hardware issues.
2025-10-17 Enhance Battery.md with monitoring and safety details
    Added detailed descriptions for battery monitoring and failsafe parameters.
2025-10-17 Update Battery.md with documentation link
    Added a link to the ArduPilot power module configuration documentation.
2025-10-17 Document ArduRover battery failsafe functionality
    Added detailed explanation of ArduRover battery failsafe features and configuration, including triggers and user actions.
2025-10-19 Revise battery failsafe documentation
    Updated the BATTERY.md file to clarify the failsafe features and parameters related to battery voltage and capacity triggers. Added notes on configurable actions and smart RTL.
2025-10-19 Fix materials checklist order in PROCEDURE.md
    Corrected the order of items in the materials checklist.
2025-10-19 Document operation modes and LED signals for ArduBoat
    Added detailed information about operation modes, driving modes, and LED indicators for ArduBoat.
2025-10-26 Revise tasks and add new entries in JOURNAL.md
    Updated tasks and added new items to the journal, including testing results and calibration warnings.
2025-11-27 Add Nicla vision battery to the journal
2025-12-22 Fix typo in battery safety switch warning
2025-12-29 Update procedure with additional materials and sections
2025-12-29 Revise materials checklist in PROCEDURE.md
    Updated materials checklist to include additional chargers.
2025-12-29 Fix typos in battery check instructions
    Corrected typos and improved clarity in battery-related instructions.
2025-12-29 Increase battery requirement to 80% for ARM procedure
    Updated battery level requirement from 60% to 80%.
2025-12-29 Update tasks in JOURNAL.md for testing payloads and sensors
    Added a task to test with a payload of 5 and 10kg and included a new task for outside sensors structure.
2025-12-29 Update JOURNAL.md with new tasks and modifications
    Added tasks for collecting videos for AI models and updated Nicla vision battery task.
2025-12-30 Update journal with new tasks and links
    Added a YouTube link for AUTO mode control and GPS point test, and included a new task regarding GPS accuracy in CAN mode wiring.
2025-12-31 Add task to buy a longer USBC cable
2025-12-31 Update JOURNAL with AQUA runtime and calibration notes
    Document AQUA runtime and battery usage details, noting calibration issue.
2026-01-21 Revise JOURNAL.md with GPS and assembly updates
    Updated journal entries with new observations and tasks related to GPS issues and Nicla Vision assembly.
2026-03-15 Update BATTERY.md with project details and references
    Added project summary, objectives, technical parameters, and bibliographic references for the Sustainable Autonomous Catamaran project.
2026-03-15 Revise battery parameters and operational guidelines
    Updated battery parameters and operational guidelines for AQUA, including capacity and voltage details.
2026-03-15 Update battery specifications and operational parameters
    Added parameters and values for battery capacity and safety triggers.
2026-03-15 Fix formatting and update battery parameters table
2026-03-15 Fix formatting in BATTERY.md table
2026-03-15 Fix formatting of CRUISE_SPEED entry in BATTERY.md
2026-03-15 Update battery parameters in BATTERY.md
    Added FS_GCS_ENABL parameter for connection loss handling.
2026-03-15 Update battery parameters and descriptions
    Clarified the purpose of FS_GCS_ENABL and added FS_GCS_TIMEOUT parameter.
2026-03-15 Revise battery parameters and state of charge table
    Updated battery parameters and safety triggers for better clarity.
2026-03-15 Revise battery specifications and runtime calculations
    Updated battery configuration details and calculations for 4S4P setup, including runtime estimations and safety parameters.
2026-03-15 Update wording for fully charged state in BATTERY.md
2026-03-15 Update battery capacity table format and headers
2026-03-20 Update battery safety trigger values in BATTERY.md
2026-03-21 Enhance BATTERY.md with inline math example
    Added inline math formatting example using delimiters.
2026-03-21 Revise battery resume parameters for AQUA system
    Updated battery parameters and specifications for AQUA setup, including voltage, capacity, and operational safety details.
2026-03-22 Fix table formatting in BATTERY.md
